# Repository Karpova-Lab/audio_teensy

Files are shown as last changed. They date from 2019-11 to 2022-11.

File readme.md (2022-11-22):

# Teensy Audio Board for pyControl
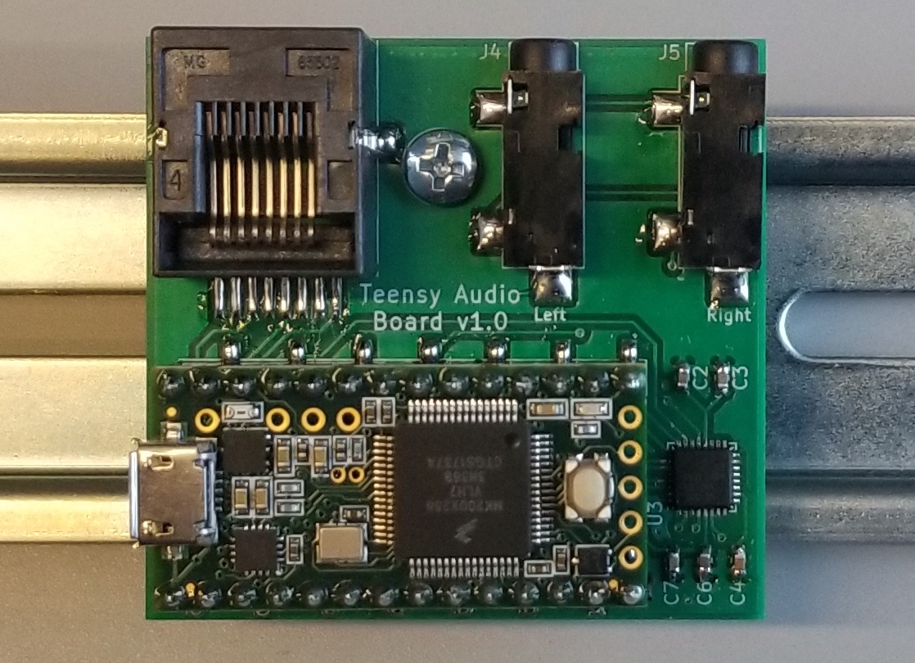
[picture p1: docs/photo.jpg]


This device connects with a [pyControl breakout](https://karpova-lab.github.io/pyControl-D-Series-Breakout/index.html) to play audio tones. 
A [Teensy 3.2](https://www.pjrc.com/teensy/index.html) generates an i2s audio signal which is later decompressed and amplified by the SGTL5000 codec IC. 
A left and right amplified signal is output to two separate mono headphone jacks. The design of this pcb is based on the [Teensy Audio Adaptor Board](https://www.pjrc.com/store/teensy3_audio.html).

## Bill Of Materials
| Qty | Reference  | Description         | Value/MPN                                                                                                            | 
|-----|------------|---------------------|----------------------------------------------------------------------------------------------------------------------|
| 3   | C2, C3, C7 | 0603 Capacitor      | [100nF](https://www.digikey.com/products/en?keywords=1276-1258-1-ND)                                                 | 
| 1   | C4         | 0603 Capacitor      | [150nF](https://www.digikey.com/product-detail/en/kemet/C0603C154K8RACTU/399-7862-1-ND/3471585)                      | 
| 2   | C5, C1     | 0603 Capacitor      | [1.0µF](https://www.digikey.com/products/en?keywords=1276-6524-1-ND)                                                 | 
| 1   | C6         | 0603 Capacitor      | [2.2µF](https://www.digikey.com/products/en?keywords=1276-1040-1-ND)                                                 | 
| 1   | FB1        | 0603 Ferrite Bead   | [600Ω @ 100MHz](https://www.digikey.com/products/en?keywords=445-2166-1-ND)                                          | 
| 1   | J1         | RJ45 Jack           | [54602-908LF](https://www.digikey.com/en/products/detail/54602-908LF/609-1046-ND/1001360)                            | 
| 2   | J3, J2     | 14pin Female Header | [SSM-114-L-SV-BE](https://www.digikey.com/products/en?keywords=SSM-114-L-SV-BE-ND)                                   | 
| 2   | J4, J5     | Mono Audio Jack     | [4832.2230](https://www.digikey.com/en/products/detail/schurter-inc/4832-2230/1731054?s=N4IgTCBcDaICwA4BsBaAzHAjAdhAXQF8g)| 
| 1   | R1         | 0603 Resistor       | [100Ω](https://www.digikey.com/products/en?keywords=311-100HRCT-ND)                                                  | 
| 2   | R3, R2     | 0603 Resistor       | [2.2KΩ](https://www.digikey.com/products/en?keywords=A130093CT-ND)                                                   | 
| 1   | U2         | 1.8V LDO Regulator  | [AP7313](https://www.digikey.com/product-detail/en/diodes-incorporated/AP7313-18SAG-7/AP7313-18SAG-7DICT-ND/2270838) | 
| 1   | U3         | Codec IC            | [SGTL5000](https://www.digikey.com/products/en?keywords=SGTL5000XNAA3R2CT-ND)                                        | 

### [View interactive BOM](https://karpova-lab.github.io/audio_teensy/ibom)

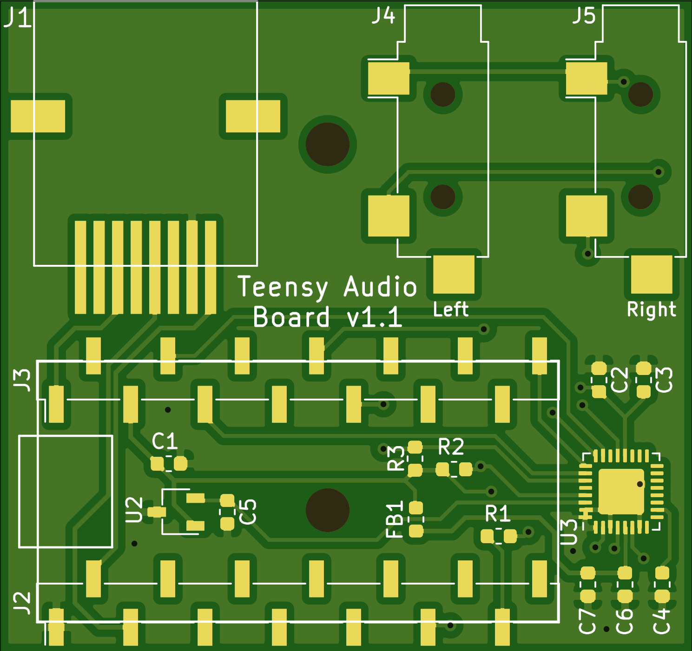
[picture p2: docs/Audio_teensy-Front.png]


## Example Firmware for Teensy
This following firmware creates 6.5KHz and 14KHz sine waves that are frequency modulated at 6.66 Hz. 
It responds to commands received over serial UART. 'L' plays the left tone, 'R' plays the right tone, 'S' stops playing both tones, 'V,5' adjust the volume to 5. 
This firmware is loaded onto the Teensy microcontroller. 

[Audio System Design Tool](https://www.pjrc.com/teensy/gui/index.html)

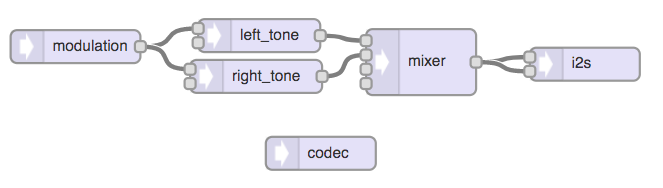
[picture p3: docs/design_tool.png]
 

```c++
#include <Audio.h>
#include <Wire.h>
#include <SPI.h>
#include <SD.h>
#include <SerialFlash.h>

// GUItool: begin automatically generated code
AudioSynthWaveformSine   modulation;     //xy=323.0056381225586,328.0056438446045
AudioSynthWaveformModulated left_tone;   //xy=530.0056648254395,308.0056457519531
AudioSynthWaveformModulated right_tone;   //xy=533.1874694824219,363.0965919494629
AudioMixer4              mixer;         //xy=719.1874771118164,330.0965805053711
AudioOutputI2S           i2s;            //xy=868.0056648254395,332.0056505203247
AudioConnection          patchCord1(modulation, 0, left_tone, 0);
AudioConnection          patchCord2(modulation, 0, right_tone, 0);
AudioConnection          patchCord3(left_tone, 0, mixer, 0);
AudioConnection          patchCord4(right_tone, 0, mixer, 1);
AudioConnection          patchCord5(mixer, 0, i2s, 0);
AudioConnection          patchCord6(mixer, 0, i2s, 1);
AudioControlSGTL5000     codec;          //xy=607.0056762695312,492.0056781768799
// GUItool: end automatically generated code

int current_waveform=0;
const int LED = 13;

void setup() {
  // put your setup code here, to run once:
  AudioMemory(10);
  codec.enable();
  codec.volume(0.10);

  modulation.frequency(20/3.0);
  modulation.amplitude(.019);

  left_tone.frequency(6500);
  left_tone.amplitude(1.0);
  right_tone.frequency(14000);
  right_tone.amplitude(1.0);

  mixer.gain(0,0);
  mixer.gain(1,0);

  current_waveform = WAVEFORM_SINE;
  left_tone.begin(current_waveform);
  right_tone.begin(current_waveform);
  Serial1.begin(9600);
  pinMode(LED,OUTPUT);
  digitalWrite(LED,LOW);
 }

void loop() {
  if (Serial1.available()){
    char msg = Serial1.read();
    if (msg=='L' | msg == 'R' | msg == 'S' | msg == 'V'){
      if (msg=='L'){ // left tone
        mixer.gain(0,1);
        mixer.gain(1,0);
        digitalWrite(LED,HIGH);
      }
      else if (msg=='R'){ //right tone
        mixer.gain(0,0);
        mixer.gain(1,1);
        digitalWrite(LED,HIGH);
      }
      else if (msg=='S'){ 
        mixer.gain(0,0);
        mixer.gain(1,0);
        digitalWrite(LED,LOW);
      }
      else if (msg=='V'){ 
        float volume = parseData();
        volume = 2*volume/100.0;
        codec.volume(volume);
      }
    }    
  }
}

int parseData(){
  char msgData[10] = "";
  Serial1.readBytesUntil('\n',msgData,10);
  char* msgPointer;
  msgPointer = strtok(msgData,",");
  return atoi(msgPointer);
}
```

## pyControl Device file

``` python
from machine import UART
from array import array

class Teensy_audio():
    def __init__(self, port):
        assert port.UART is not None, '! Teensy Audio Player needs a port with UART.'
        self.uart = UART(port.UART, 9600)
        self.uart.init(9600, bits=8, parity=None, stop=1, timeout=1)
        self.uart.write('S')

    def play(self, side):
        if side == 'Left':
            self.uart.write('L')
        elif side == 'Right':
            self.uart.write('R')
        return True

    def stop(self):
        self.uart.write('S')
        return False

    def set_volume(self, volume): # Between 1 - 65
        self.uart.write('V,{}'.format(volume))
```

## Latency
The start and stop latencies are both about 6.5 ± 1 ms

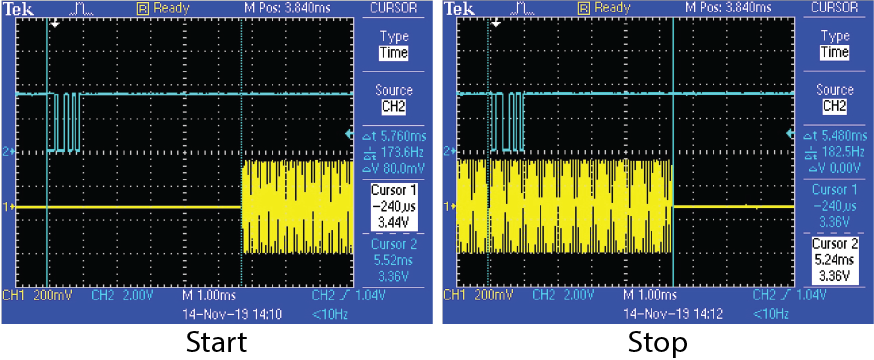
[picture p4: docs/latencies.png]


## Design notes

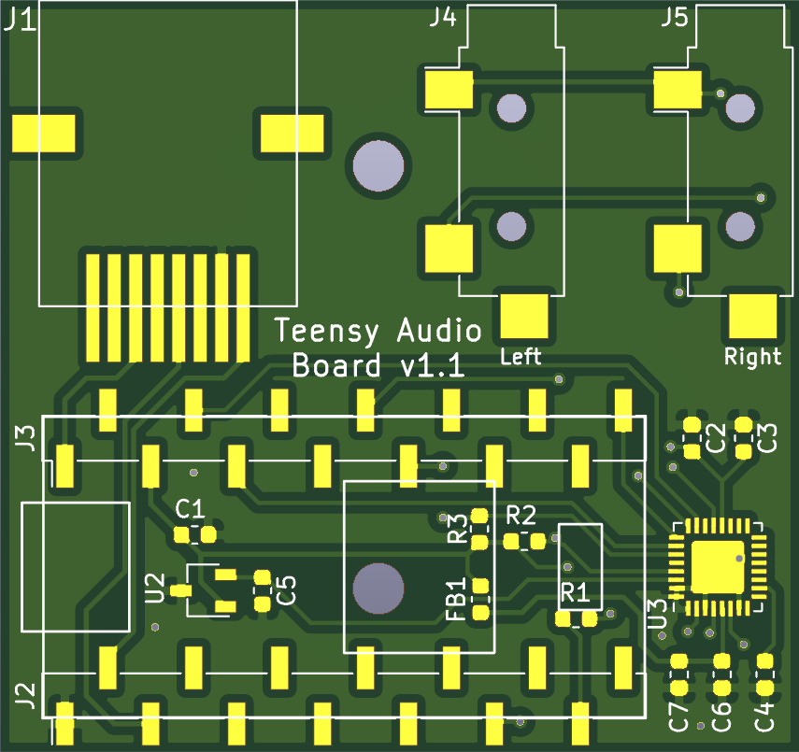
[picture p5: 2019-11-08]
docs/render.png

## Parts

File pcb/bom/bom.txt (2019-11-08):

"Qty","Reference","Description","Value/MPN","Purchase Link"
"3","C2, C3, C7","0603 Capacitor","100nF","https://www.digikey.com/products/en?keywords=1276-1258-1-ND"
"1","C4","0603 Capacitor","150nF","https://www.digikey.com/product-detail/en/kemet/C0603C154K8RACTU/399-7862-1-ND/3471585"
"2","C5, C1","0603 Capacitor","1.0µF","https://www.digikey.com/products/en?keywords=1276-6524-1-ND"
"1","C6","0603 Capacitor","2.2µF","https://www.digikey.com/products/en?keywords=1276-1040-1-ND"
"1","FB1","0603 Ferrite Bead","600Ω @ 100MHz","https://www.digikey.com/products/en?keywords=445-2166-1-ND"
"1","J1","RJ45 Jack","0855025008","https://www.digikey.com/products/en?keywords=WM3547CT-ND"
"2","J3, J2","14pin Female Header","SSM-114-L-SV-BE","https://www.digikey.com/products/en?keywords=SSM-114-L-SV-BE-ND"
"2","J4, J5","Mono Audio Jack","MJ-3523-SMT","https://www.digikey.com/products/en?keywords=CP-3523MJCT-ND"
"1","R1","0603 Resistor","100Ω","https://www.digikey.com/products/en?keywords=311-100HRCT-ND"
"2","R3, R2","0603 Resistor","2.2KΩ","https://www.digikey.com/products/en?keywords=A130093CT-ND"
"1","U2","1.8V LDO Regulator","AP7313","https://www.digikey.com/product-detail/en/diodes-incorporated/AP7313-18SAG-7/AP7313-18SAG-7DICT-ND/2270838"
"1","U3","Codec IC","SGTL5000","https://www.digikey.com/products/en?keywords=SGTL5000XNAA3R2CT-ND"

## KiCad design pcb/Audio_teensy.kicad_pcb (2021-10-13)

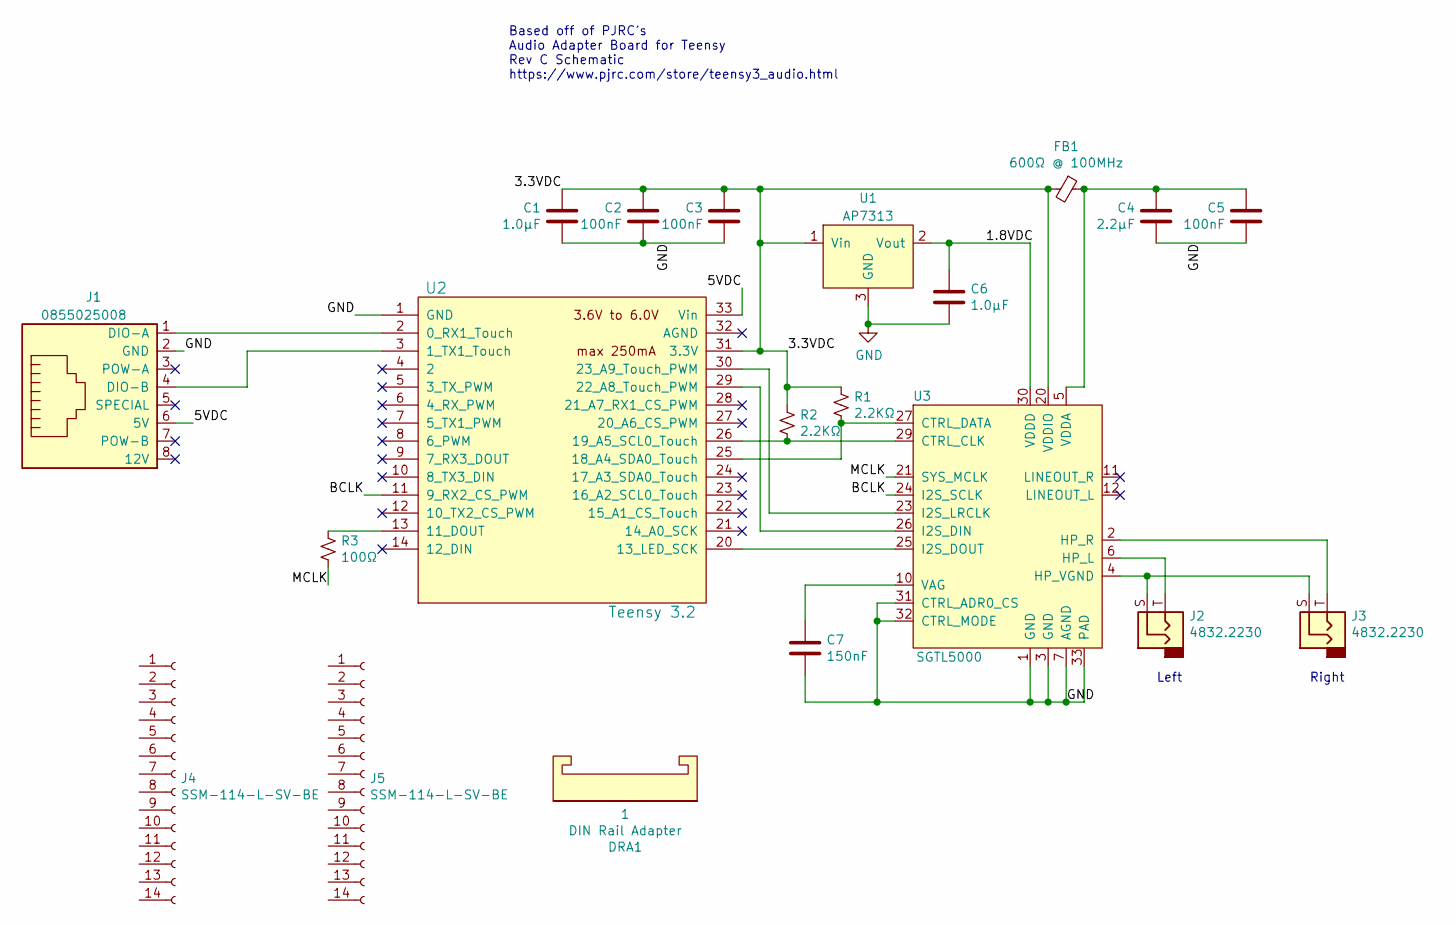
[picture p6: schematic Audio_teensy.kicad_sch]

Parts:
C1, C6: 1.0µF; C_0603_1608Metric
C2, C3, C5: 100nF; C_0603_1608Metric
C4: 2.2µF; C_0603_1608Metric
C7: 150nF; C_0603_1608Metric
DRA1: DIN Rail Adapter; DIN_Clip
FB1: 600Ω @ 100MHz; C_0603_1608Metric
J1: 0855025008; RJ45_THP_Vertical
J2, J3: 4832.2230; mono_jack_throughhole
J4, J5: SSM-114-L-SV-BE; PinHeader_1x14_P2.54mm_Vertical_SMD_Pin1Left
R1, R2: 2.2KΩ; R_0603_1608Metric
R3: 100Ω; R_0603_1608Metric
U1: AP7313; TSOT-23
U2: Teensy 3.2; Teensy30_31_32_LC_SMD
U3: SGTL5000; QFN-32-1EP_5x5mm_P0.5mm_EP3.1x3.1mm

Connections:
/1.8VDC: C6.1, U1.2 (Vout), U3.30 (VDDD)
/3.3VDC: C1.2, C2.2, C3.2, FB1.2, R1.1, R2.1, U1.1 (Vin), U2.31 (3.3V), U3.20 (VDDIO)
/5VDC: J1.6 (5V), U2.33 (Vin)
/BCLK: U2.11 (9_RX2_CS_PWM), U3.24 (I2S_SCLK)
/MCLK: R3.2, U3.21 (SYS_MCLK)
GND: C1.1, C2.1, C3.1, C4.1, C5.1, C6.2, C7.2, J1.2 (GND), U1.3 (GND), U2.1 (GND), U3.1 (GND), U3.3 (GND), U3.7 (AGND), U3.31 (CTRL_ADR0_CS), U3.32 (CTRL_MODE), U3.33 (PAD)
unnamed: C4.2, C5.2, FB1.1, U3.5 (VDDA)
unnamed: C7.1, U3.10 (VAG)
unnamed: J1.1 (DIO-A), U2.2 (0_RX1_Touch)
unnamed: J1.4 (DIO-B), U2.3 (1_TX1_Touch)
unnamed: J2.S, J3.S, U3.4 (HP_VGND)
unnamed: J2.T, U3.6 (HP_L)
unnamed: J3.T, U3.2 (HP_R)
unnamed: R1.2, U2.25 (18_A4_SDA0_Touch), U3.27 (CTRL_DATA)
unnamed: R2.2, U2.26 (19_A5_SCL0_Touch), U3.29 (CTRL_CLK)
unnamed: R3.1, U2.13 (11_DOUT)
unnamed: U2.20 (13_LED_SCK), U3.25 (I2S_DOUT)
unnamed: U2.29 (22_A8_Touch_PWM), U3.26 (I2S_DIN)
unnamed: U2.30 (23_A9_Touch_PWM), U3.23 (I2S_LRCLK)

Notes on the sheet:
Based off of PJRC’s Audio Adapter Board for Teensy Rev C Schematic https://www.pjrc.com/store/teensy3_audio.html
Left
Right

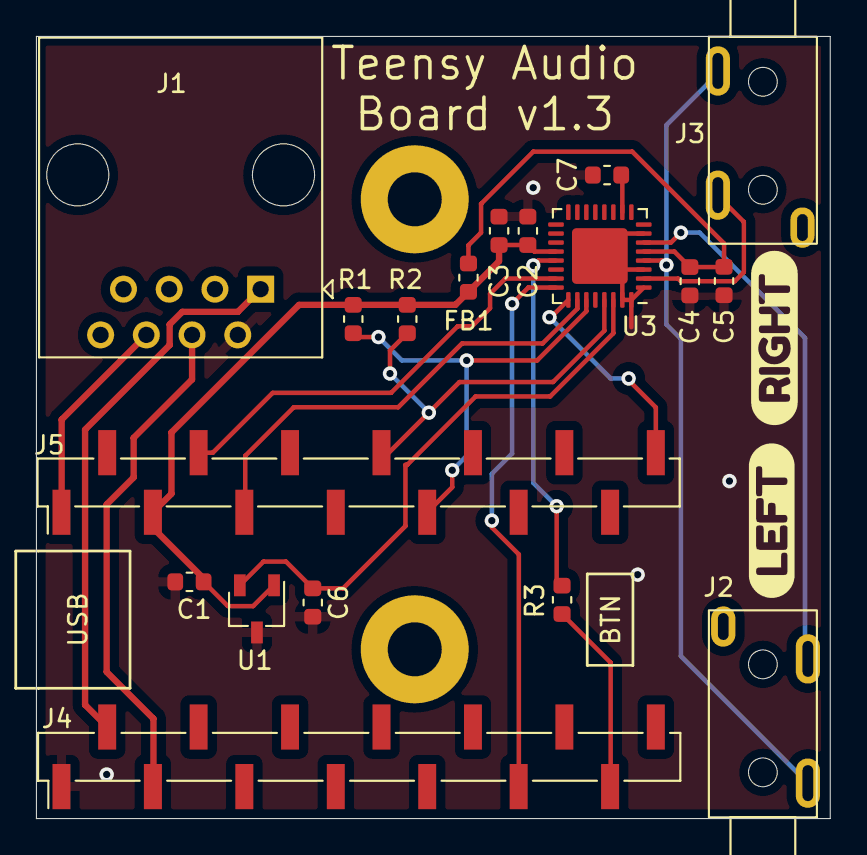
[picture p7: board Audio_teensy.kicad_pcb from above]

Board: 2 copper layers, 44.1 x 43.5 mm, 22 parts (0 on the bottom side), 19 nets.

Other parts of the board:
svg2mod, svg2mod#2: G***; svg2mod

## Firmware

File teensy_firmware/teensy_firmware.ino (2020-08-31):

#include <Audio.h>
#include <Wire.h>
#include <SPI.h>
#include <SD.h>
#include <SerialFlash.h>

// GUItool: begin automatically generated code
AudioSynthWaveformSine   modulation;     //xy=405,328
AudioSynthSimpleDrum     bloop_tone;          //xy=585,409
AudioSynthWaveformModulated left_tone;      //xy=590,314
AudioSynthWaveformModulated right_tone;     //xy=592,355
AudioMixer4              mixer;          //xy=791,371
AudioOutputI2S           i2s;            //xy=940,373
AudioConnection          patchCord1(modulation, 0, left_tone, 0);
AudioConnection          patchCord2(modulation, 0, right_tone, 0);
AudioConnection          patchCord3(bloop_tone, 0, mixer, 2);
AudioConnection          patchCord4(left_tone, 0, mixer, 0);
AudioConnection          patchCord5(right_tone, 0, mixer, 1);
AudioConnection          patchCord6(mixer, 0, i2s, 0);
AudioConnection          patchCord7(mixer, 0, i2s, 1);
AudioControlSGTL5000     codec;          //xy=707,513
// GUItool: end automatically generated code



int current_waveform=0;
const int LED = 13;

void setup() {
  // put your setup code here, to run once:
  AudioMemory(10);
  codec.enable();
  codec.volume(0.10);

  modulation.frequency(20/3.0);
  modulation.amplitude(.019);

  left_tone.frequency(6500);
  left_tone.amplitude(1.0);
  right_tone.frequency(14000);
  right_tone.amplitude(1.0);

  
  bloop_tone.frequency(2000);
  bloop_tone.length(100);
  bloop_tone.secondMix(0.0);
  bloop_tone.pitchMod(0.3);

  mixer.gain(0,0);
  mixer.gain(1,0);
  mixer.gain(2,0);

  current_waveform = WAVEFORM_SINE;
  left_tone.begin(current_waveform);
  right_tone.begin(current_waveform);
  Serial1.begin(9600);
  pinMode(LED,OUTPUT);
  digitalWrite(LED,LOW);
 }

void loop() {
  if (Serial1.available()){
    char msg = Serial1.read();
    if (msg=='L' | msg == 'R' | msg == 'S' | msg == 'V' | msg == 'B'){
      if (msg=='L'){ // left tone
        mixer.gain(0,1);
        mixer.gain(1,0);
        mixer.gain(2,0);
        digitalWrite(LED,HIGH);
      }
      else if (msg=='R'){ //right tone
        mixer.gain(0,0);
        mixer.gain(1,1);
        mixer.gain(2,0);
        digitalWrite(LED,HIGH);
      }
      else if (msg=='S'){ 
        mixer.gain(0,0);
        mixer.gain(1,0);
        mixer.gain(2,0);
        digitalWrite(LED,LOW);
      }
      else if (msg=='B'){ 
        mixer.gain(0,0);
        mixer.gain(1,0);
        mixer.gain(2,1);
        bloop_tone.noteOn();
        digitalWrite(LED,HIGH);
        delay(50);
        digitalWrite(LED,LOW);
      }
      else if (msg=='V'){ 
        float volume = parseData();
        volume = 2*volume/100.0;
        codec.volume(volume);
      }
    }    
  }
}

int parseData(){
  char msgData[10] = "";
  Serial1.readBytesUntil('\n',msgData,10);
  char* msgPointer;
  msgPointer = strtok(msgData,",");
  return atoi(msgPointer);
}

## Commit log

2019-10-30 added teensy to library
2019-11-02 working prototype
2019-11-08 v1.1 AP3713 regulator pins were mapped incorrectly to footprint. Swapped Vin and GND. Added descriptions and purchase links for all components.
    [Audio_teensy.kicad_pcb, Audio_teensy.sch, bom.xlsx]
2019-11-14 Adjusted modulation wave. LED now indicates whether tone is being played.
2019-11-15 renamed teensy firmware
2019-11-15 updated readme. cleaned up teensy code
2021-09-01 upgrade to kicad 5.99
    [Audio_teensy.kicad_pcb, Audio_teensy.kicad_sch, Audio_teensy.sch]
2021-09-01 moved kicad files up into PCB folder
    [Audio_teensy.kicad_pcb, Audio_teensy.kicad_sch, bom.xlsx]
2021-09-02 changed to through hole components
    rearranged mono jacks to point towards opposite sides
    [Audio_teensy-B_Cu.gbr, Audio_teensy-B_Mask.gbr, Audio_teensy-B_Paste.gbr, Audio_teensy-B_Silkscreen.gbr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]
2021-10-13 pcb v1.3
    [Audio_teensy-B_Cu.gbr, Audio_teensy-B_Mask.gbr, Audio_teensy-B_Paste.gbr, Audio_teensy-B_Silkscreen.gbr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]
2022-11-22 BOM update to reflect changes in PCB v1.3
